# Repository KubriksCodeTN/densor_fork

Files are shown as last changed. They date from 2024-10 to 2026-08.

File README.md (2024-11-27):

# Densor



## About the project

Densor is an intraoral sensor platform, attached to regular dental retainers or aligners, that can take measurements inside the mouth. 

## Rationale

At present, in mouth measurements are typically made with external tools and in a controlled labaratory setting. Thus, real data from users daily lives is missing. To overcome this, we propose using widely used deltal retainers (or aligners), and enhance them with the Densor sensing platform. This way data is collected from inside the mouth without external tools. 

## Features

1. **Contactless transmission:** Densor is completely sealed and interacts with a smartphone via [NFC protocol](https://en.wikipedia.org/wiki/Near-field_communication). 
2. **Energy harvesting:** To stay powered Densor harvests energy, either from the [NFC communication itself](https://github.com/TUDSSL/densor/tree/master/NFC_harvester_battery_free) or from the [temperature gradient between the body and cold water](https://github.com/TUDSSL/densor/tree/master/TEG_harvester_battery_free). 
4. **Free of external hardware:** Operating Densor does not require any specialized tools, other than a NFC-compatible smartphone.

## Project layout

This repository contains the design (both hardware and software) of two versions of Densor, based on the source of energy harvesting. Each version of the project is contained in its own folder:

1. **[Densor with NFC-based energy harvesting from a smartphone](https://github.com/TUDSSL/densor/tree/master/NFC_harvester_battery_free)**, as presented in [this research article](https://dl.acm.org/doi/10.1145/3699746);
2. **[Densor with thermoelectric energy harvesting from drinking cold water](https://github.com/TUDSSL/densor/tree/master/TEG_harvester_battery_free)**.

 

## Copyright

Copyright (C) 2024 TU Delft Embedded Systems Group/[Sustainable Systems Laboratory](https://github.com/TUDSSL).

MIT License or otherwise specified. See [license](https://github.com/TUDSSL/densor/blob/master/LICENSE.txt) file for details.

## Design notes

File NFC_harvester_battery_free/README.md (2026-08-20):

# Densor with NFC-based Energy Harvesting from a Smartphone

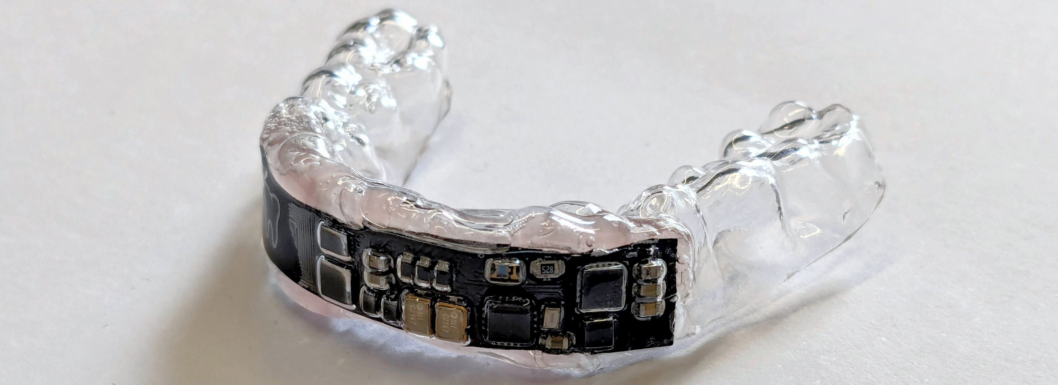
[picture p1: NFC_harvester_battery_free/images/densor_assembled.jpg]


This is the official public repository for intraoral sensing platform, called Densor (a portmanteau of a word _dental_ and _sensor_), based on [NFC protocol](https://en.wikipedia.org/wiki/Near-field_communication) for energy harvesting and communication from a NFC-enabled smartphone. For a Densor version with thermoelectric energy harvesting from drinking cold water please refer to [this repository](https://github.com/TUDSSL/densor/tree/master/TEG_harvester_battery_free). 

## About the Project

This repository contains the design files of the NFC-based Densor:

- [Densor hardware](https://github.com/TUDSSL/densor/tree/master/NFC_harvester_battery_free/hardware)
- [Densor firmware](https://github.com/TUDSSL/densor/tree/master/NFC_harvester_battery_free/software/DentalSensor_StorageProject)
- [Android app](https://github.com/TUDSSL/densor/tree/master/NFC_harvester_battery_free/software/source_ST25NFCApplication_V3_9)
- [Experiment setup and data collected from Densor evaluation](https://github.com/TUDSSL/densor/tree/master/NFC_harvester_battery_free/data/experiments) presented in Densor's [accompanying publciation](https://dl.acm.org/doi/10.1145/3699746).

## Rationale behind Densor

Intraoral sensors are another type of sensors in the field of healthcare and technology. While head-worn wearables have made significant advancements in monitoring various health metrics, placing sensors directly in the mouth remains a challenge. Currently, we rely heavily on external tools to gather dental and oral health data, which leaves critical information missing. For those looking to deploy in-mouth sensors, the process is daunting, requiring them to start from scratch. Additionally, there is no straightforward way to keep these sensors small, safe, and capable of long-lasting communication, making it difficult to integrate them into practical applications.

## Challenges

Intraoral sensing is unique because it operates within one of the most dynamic and challenging environments in the human body—the mouth. Unlike other forms of wearable technology, intraoral sensors must contend with constant exposure to saliva, varying temperatures, and the mechanical forces of chewing and speaking. These sensors need to be not only highly sensitive and accurate but also biocompatible and safe for long-term use. Additionally, they offer the potential to gather real-time data on oral health, dietary habits, and even health conditions, providing insights that are difficult to obtain through external sensors. This makes intraoral sensing a powerful tool with unique capabilities that go beyond existing methods.

## Densor Architecture

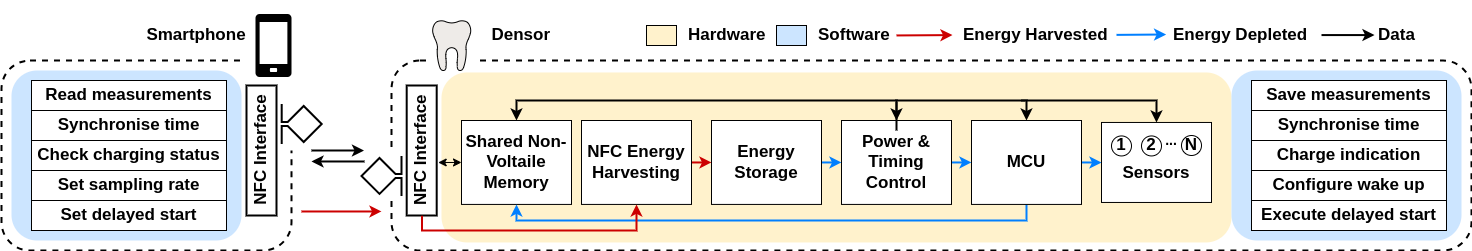
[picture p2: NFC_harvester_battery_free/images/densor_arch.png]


### Communication and Data Storage

Densor uses the NFC interface (based on STMicroelectronics' [ST25DV64K](https://www.st.com/en/nfc/st25dv64k.html) NFC/RFID tag IC) for communication with a smartphone, and the on board non-voltatile memory to store measurements. This way, data collected by Densor is always available to be read out by the smartphone.

### Energy Harvesting

Energy is harvested from the NFC tag itself, and stored for later use. This allows for Densor's continous operation and reader-independent data collection.

### Energy Storage

The harvested energy is stored on capacitors instead of batteries. This makes Densor a battery-free device and thus safer and more acceptable than Densor based on batteries.

### Power Control

Despite using low-power sensors, energy would be drained from the storage capacitor(s) rapidly if Densor is kept continuously powered. As the harvested energy stored on the capacitors is limited, it is imperative that we save and expend this power carefully. To overcome this, we use a low power Real-Time Clock (RTC) [AB1805](https://abracon.com/Precisiontiming/AB18X5-RTC.pdf) with power switch for power management. This means that the microcontroller unit (MCU) and sensors are completely powered off in the inter-sample period, with only the RTC powered to determine wake up time. This method achieves better power saving than deep-sleep or any of the low power run modes of the MCU.

### Densor On-Board Sensors

As of now, Densor includes three sensing modalities: temperature, accelaration and light intensity. Measuring oral temperature, jaw position, and whether the mouth is open using intraoral sensors is useful for gaining insight into oral and overall health. Oral temperature sensors provide accurate readings to detect early signs of fever and inflammation. Jaw position sensors can monitor alignment and movement, making them valuable for detecting sleep patterns. Light sensors that detect whether the mouth is open can help track breathing patterns and oral habits, which are essential for identifying issues like mouth breathing or sleep-related disorders.

## Densor Operation

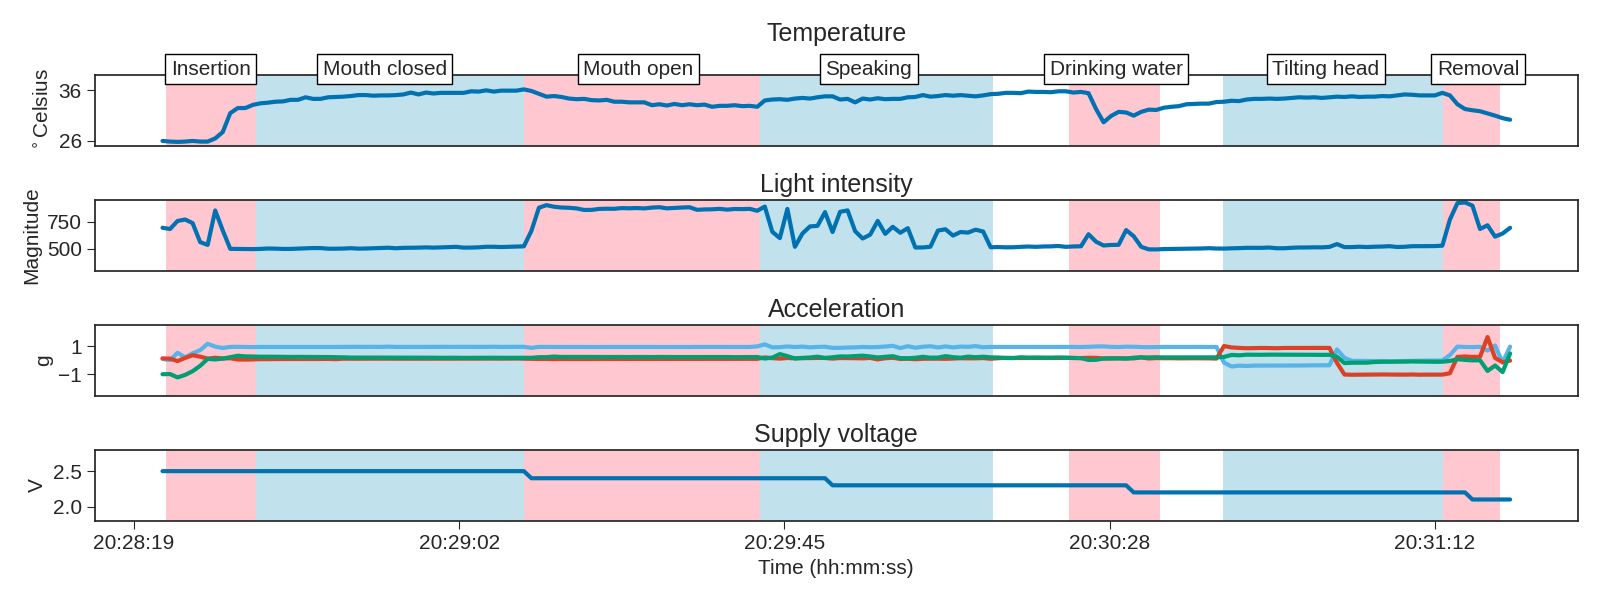
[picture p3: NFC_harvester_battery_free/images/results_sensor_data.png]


The above image shows examples of data collected by Densor and demonstrates its capabilities. The temperature can be seen rising to body temperature when Densor is inserted in the mouth. The light level falls when the mouth is closed, and rises when the mouth is open. It also varies when the user is speaking. When drinking cold water, the temperature initally falls and then rises back to body temperature.

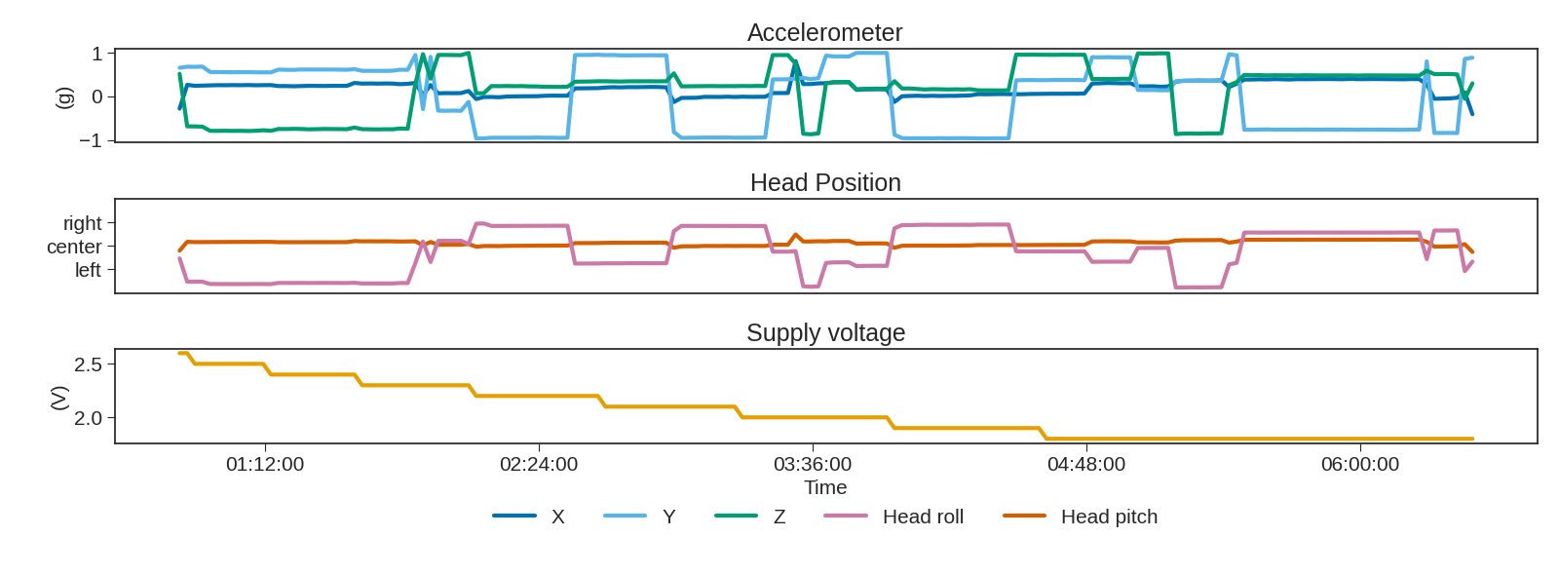
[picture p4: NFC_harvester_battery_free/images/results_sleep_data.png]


Densor can also determine the orientation of the jaw when the head is tilted. This is particularly useful for measuring head position during sleep, as seen in the above figure. The figure shows actual data collected from a user during a full night's sleep with _one sample collected every two minutes_. We can see the orientation of the head change between left, right and center as the user changes their sleep position.

## Getting Started with Densor

The long-term goal of the Densor project is to lower the ceiling of development of intraoral sensors. Thus, we wish that everyone can build, use and even expand Densor to improve sensing capabilities and data collection. Here we explain the steps to create Densor from scratch.

### Building the Densor Hardware

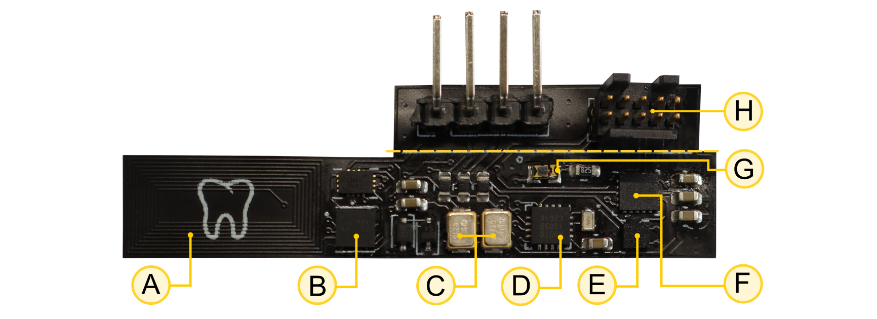
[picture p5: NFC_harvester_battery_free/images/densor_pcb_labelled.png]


The Densor printed circuit board (PCB) is built using off-the-shelf components and assembled onto a flexible PCB. In our case we have used the flex PCB services from [PCBway](https://www.pcbway.com/fpc-rigid-flex-pcb/flex-pcb.html). The picture above shows the main components of Densor ( (a comprehensive list of Densor hardware, along with links to buy them, can be found under [Hardware](https://github.com/TUDSSL/densor/tree/master/NFC_harvester_battery_free/hardware)).

- **A** Custom-designed PCB antenna
- **B** STMicroelectronics [ST25DV64K](https://www.st.com/en/nfc/st25dv64k.html) NFC tag
- **C** Seiko [CPH3225A](https://www.sii.co.jp/en/me/datasheets/chip-capacitor/cph3225a/) chip capacitor bank
- **D** Abracon [AB1805](https://abracon.com/Precisiontiming/AB18X5-RTC.pdf) RTC
- **E** STMicroelectronics [LIS2DW12](https://www.st.com/en/mems-and-sensors/lis2dw12.html) accelerometer
- **F** STMicroelectronics [STM32L021F4](https://www.st.com/en/microcontrollers-microprocessors/stm32l021f4.html) MCU
- **G** Vishay [VEMD1060X01](https://www.vishay.com/docs/84295/vemd1060x01.pdf) photodiode
- **H** Serial Wire Debug (SWD) programming port (which is cut off before embedding in a dental aligner).
- **I** TI [TMP117](https://www.ti.com/lit/ds/symlink/tmp117.pdf) temperature sensor

The [Densor hardware](https://github.com/TUDSSL/densor/tree/master/NFC_harvester_battery_free/hardware) folder contains the [gerber files](https://github.com/TUDSSL/densor/tree/master/NFC_harvester_battery_free/hardware/gerbers_schematic) which can be used to order the PCBs directly. To order directly, use the `.gbr` Gerber output files and `.drl` drill file for manufacturing.

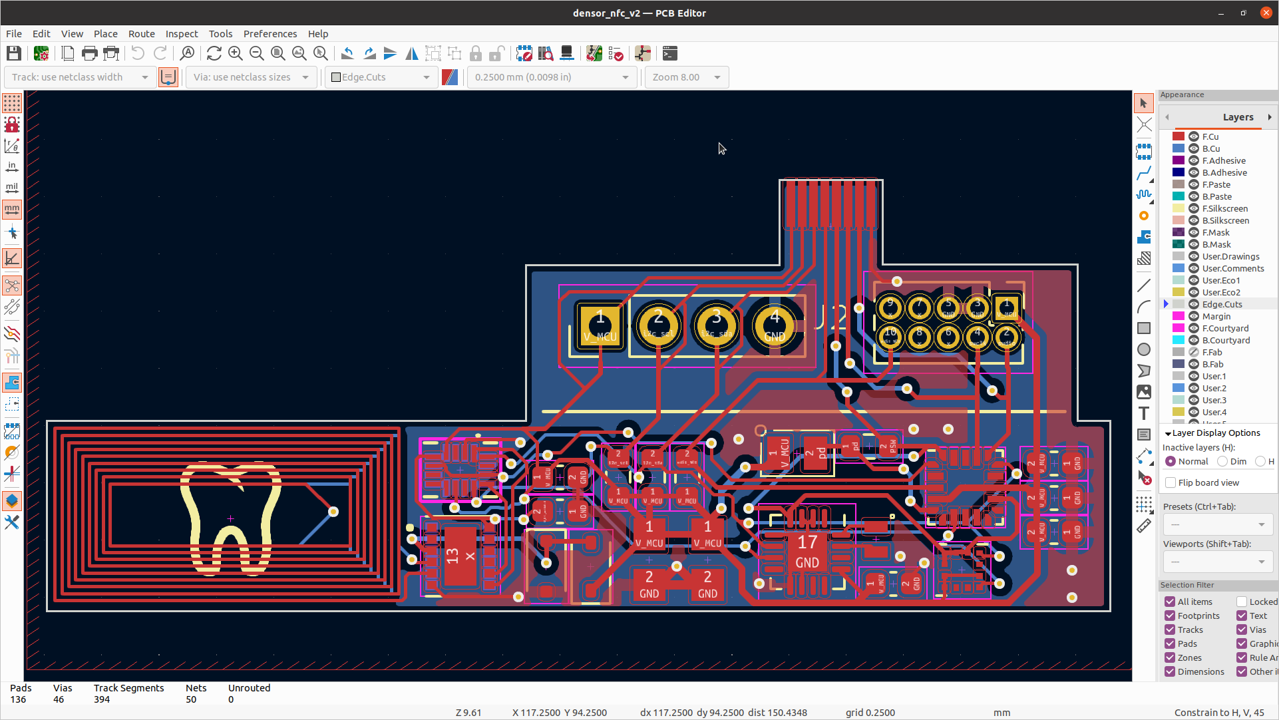
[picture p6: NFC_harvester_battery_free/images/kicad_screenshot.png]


The hardware folder also contains Densor' [schematic](https://github.com/TUDSSL/densor/tree/master/NFC_harvester_battery_free/hardware/gerbers_schematic) and [KiCad](https://www.kicad.org/blog/2021/12/KiCad-6.0.0-Release/) project which can be used for further expansion or modifications of Densor. A screenshot of the Densor PCB design in KiCad can be seen above. To open the project using Kicad, launch Kicad and navigate to 'File' -> 'Open project' -> And choose the [`densor_nfc_v2.kicad_pro`](https://github.com/TUDSSL/densor/blob/master/NFC_harvester_battery_free/hardware/Densor_kicad_project/densor_nfc_v2.kicad_pro) project file. The project includes the KiCad project files `.kicad_pcb`, `.pro` and `.sch`.

With the PCB and components, we used the lead-free [SAC305](https://nl.mouser.com/datasheet/2/73/SMD291SNL250T3-595229.pdf) solder paste to assemble the Densor as per the schematic.

### Uploading the Firmware to Densor's MCU

Once the Densor hardware is assembled, the [STM32L021F4](https://www.st.com/en/microcontrollers-microprocessors/stm32l021f4.html) MCU on board the Densor needs to have the firmware uploaded. The Densor [software folder](https://github.com/TUDSSL/densor/tree/master/NFC_harvester_battery_free/software/DentalSensor_StorageProject) contains the [STM32CubeIDE](https://www.st.com/en/development-tools/stm32cubeide.html)-based project is required for this. The firmware is uploaded using a [J-Link Debug probe](https://www.segger.com/products/debug-probes/j-link/) and a 10-pin header.

_Note:_ The current version of the PCB also has an [5034800800 FPC connector](https://www.molex.com/en-us/products/part-detail/5034800800) with all SWD signals which can also be used for programming.

### Memory Layout and Pinout

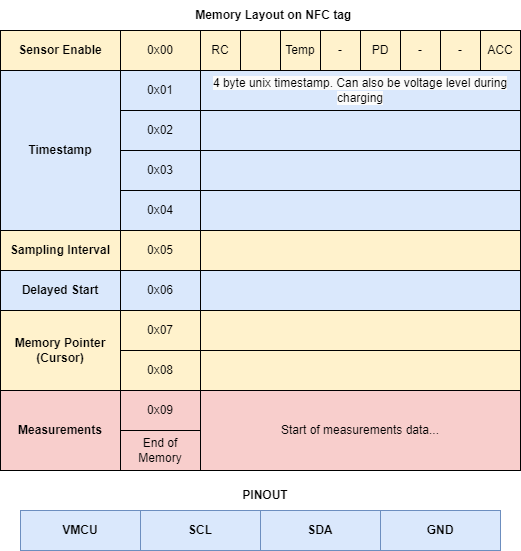
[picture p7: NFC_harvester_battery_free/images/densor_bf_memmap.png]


### Using the Densor Smartphone App

With the firmware uploaded to the MCU, the Densor is ready to be uses. This can be verified with an Android-based smartphone running the Densor [smartphone app](https://github.com/TUDSSL/densor/tree/master/NFC_harvester_battery_free/software/source_ST25NFCApplication_V3_9). The app (screenshot below) is built using Android Studio and can interact with the assembled Densor PCB via NFC. Detailed instructions on how to build the app can be found [here](https://github.com/TUDSSL/densor/tree/master/NFC_harvester_battery_free/software/source_ST25NFCApplication_V3_9).

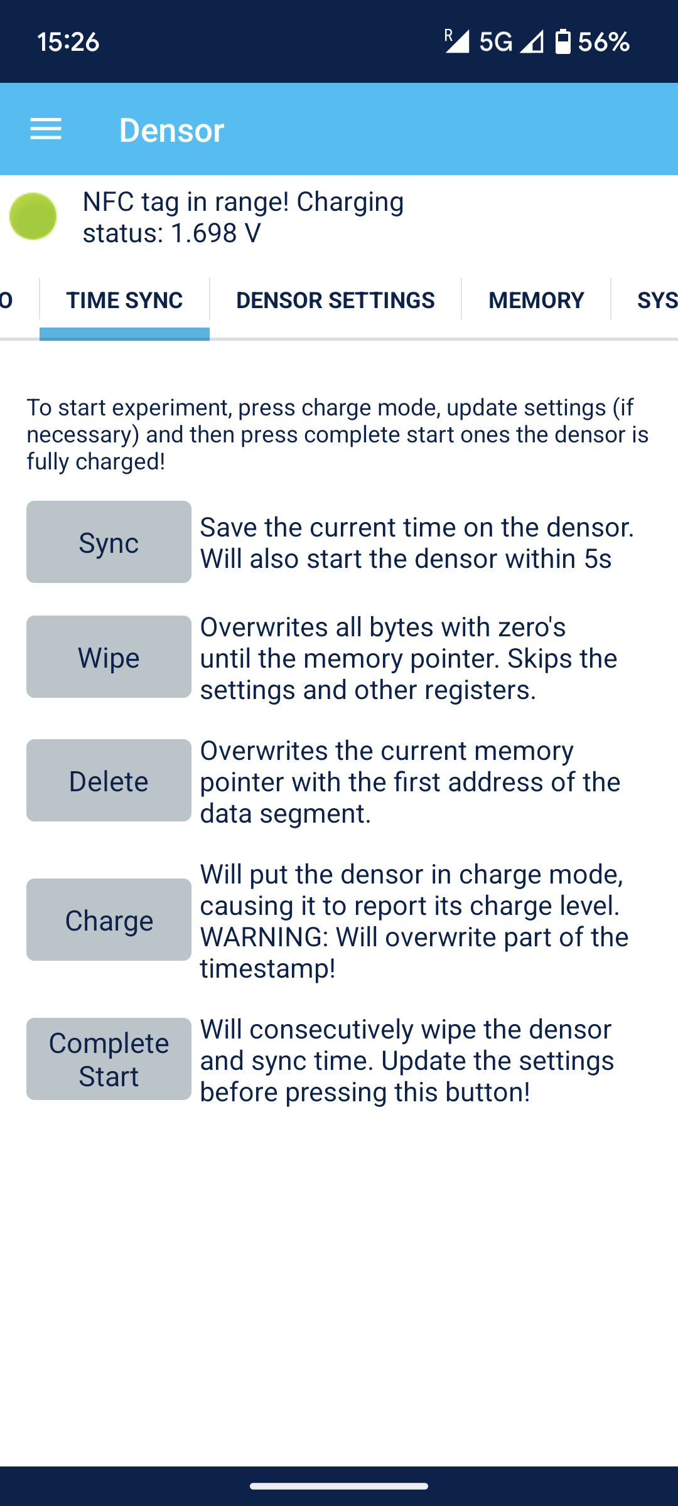
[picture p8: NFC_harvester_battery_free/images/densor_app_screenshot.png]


### Attaching Densor to Aligners using Epoxy

Finally, the Densor PCB has to be attached to the retiners or aligners. Clear plastic vaccum formed [retainers](https://en.wikipedia.org/wiki/Retainer_(orthodontics)) are widely used in orthodontic treatment. They can easily be fabricated with the help of a dental technician.

In our Densor fabrication process, first a [dental impression](https://en.wikipedia.org/wiki/Dental_impression) of each test subject was taken using [condensation silicone](https://products.coltene.com/EN/US/products/prosthetics/c-silicones/speedex/speedex-putty) placed on a dental impression tray. The hardened impression was later used to create a [plaster model](https://bredent-group.com/wp-content/uploads/2020/06/gipse-von-hoechster-Qualitaet_000727GB-20150601.pdf) of the subject's lower jaw teeth. Next, the plaster was placed inside an [Erkoform-3d+ dental  thermoforming unit](https://www.erkodent.de/en/product/?id=521210). Then, a dental [thermoforming plate](https://www.erkodent.de/wp-content/documents/products/thermoprosp_EN.pdf) was heated to 160 degrees Celcius by Erkoform-3d+, placed over the dental plaster and vacuum sealed. After vacuum sealing, all redundant and sharp edges of the fabricated aligner were removed by the cut-off wheel. The remaining imperfections were removed with the same cut-off wheel, and finally disinfected.

We used a [food safe epoxy](https://polyestershoppen.com/epoxy/voedselveilige-epoxy-419.html) to attach the assembled Densor PCB to the retainers. The epoxy has to be carefully mixed in a 10:6 ratio of resin and hardner, and applied over the PCB with a brush. The epoxy takes a _full five days to cure completely_ and must not be used before that even though it appears to have hardened.

**Once the epoxy is fully cured, Voila! You Densor is ready to use**.

## How to Operate Densor

To use Densor, begin with the smartphone app, and fully assembled Densor.

### Starting and Stopping Densor

_Step 1._ When you hold Densor close to the smartphone such that both NFC antennas of a Densor and a smartphone align, the app will launch automatically and Densor will begin charging.

_Step 2._ The capacitor's charged voltage will be displayed in the app. While Densor theoretically supports 3.3 V maximum capacitor voltage, in practice, it reaches about 2.6 V.

_Step 3._ To configure the on-board Densor sensors, go to the settings tab. Here, you can enable specific sensors, select the sampling rate, and set an optional delayed start. Click the `Update` button to apply these settings to the sensor.

_Step 4._ The Densor will only begin measuring once the time is synced. In the `Time Sync` tab, click the `Sync` button to start the sensor from the current time. The `Wipe` button deletes all previously collected data, while `Delete` resets the cursor without overwriting previous data with zeros.

_Step 5._ To stop the sensor, switch to `Charge` mode. This will revert the sensor to showing feedback on the charging voltage reached. _Note:_ This will also reset the timestamp. Please save measurements before putting Densor to charge mode.

### Reading the Data

_Step 1._ To save the data, go to the `Memory` tab and click `Dump memory to file`. In the 'Destination folder' field, enter your desired file name, then click `OK`. The data will be saved as a `.bin` file on your phone. The file is located in the 'Downloads' folder of the internal memory.

_Step 2._ To analyse this data, use the provided scripts avaible in the [data folder](https://github.com/TUDSSL/densor/tree/master/NFC_harvester_battery_free/data) of this repository.

_Step 3._ If the [experiment master](https://github.com/TUDSSL/densor/blob/master/NFC_harvester_battery_free/data/experiments/experiment_master_ui.py) script was used to generate the data as per a protocol, then place the generated `.bin` file in the [data dumps folder](https://github.com/TUDSSL/densor/tree/master/NFC_harvester_battery_free/data/experiments/data_dumps), and view the results with the [plot_labelled.py](https://github.com/TUDSSL/densor/blob/master/NFC_harvester_battery_free/data/experiments/plot_labeled.py) script. Make sure to use the [environment](https://github.com/TUDSSL/densor/blob/master/NFC_harvester_battery_free/data/environment.yml) provided.

## Collecting New Data

Data collected using Densor can be labelled and stored using the scripts in the [data folder](https://github.com/TUDSSL/densor/tree/master/NFC_harvester_battery_free/data/experiments).

1. **Using a predefined experiment protocol:** You can use a set of [existing experiment protocols](https://github.com/TUDSSL/densor/tree/master/NFC_harvester_battery_free/data/experiments/experiment_protocols) or create a new `.json` file to decide the tasks that will be performed while labeling data collected by Densor.
2. **Executing an experiment:** Run the [`experiment_master_ui.py`](https://github.com/TUDSSL/densor/blob/master/NFC_harvester_battery_free/data/experiments/experiment_master_ui.py) file to launch the instructing script. Perform the actions as instructed by the script for the prescribed duration.

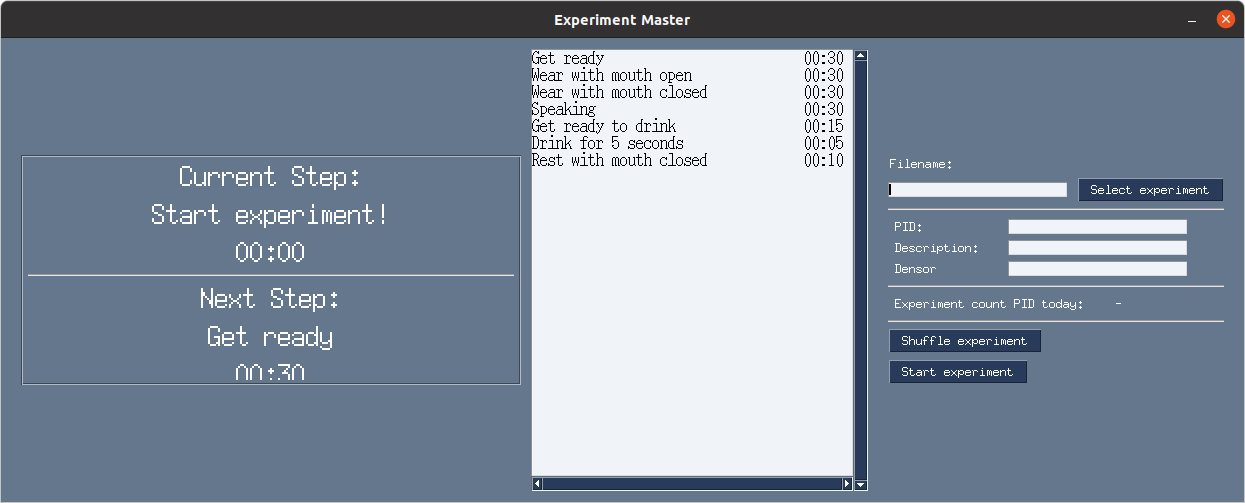
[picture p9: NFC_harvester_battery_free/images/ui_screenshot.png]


3. **Save the data:** Save the data using the smartphone app with the name prompted by the script to a `.bin` file and place it in the [data_dumps](https://github.com/TUDSSL/densor/tree/master/NFC_harvester_battery_free/data/experiments/data_dumps) folder.
4. **Label and view the data:** Run the `data_labeller.py` script to label the data for further machine learning tasks, or `plot_labelled.py` file to view the data.

## Frequently Asked Questions

**1. How long does it take to charge Densor?**

It takes approximately a minute to charge Densor using a smartphone. The exact charging time depends on how well the antennas of Densor and the smartphone align. The exact charging voltage of the capacitors can be read on the app for feedback.

**2. How long does Densor run when fully charged?**

Densor's lifetime depends on the sampling rate and number of capacitors used. For example, when using two capacitors and sampling once every two minutes Densor lasts for about 7 hours on a single charge. To increase the lifetime, more capacitors can be added. This will however change the charging behavior as well.

**3. Is Densor comfortable to wear?**

In our opinion, the experience of using Densor is no different than using retainers. Thus, if using retainers/aligners anyway, Densor should cause no additional discomfort beyond usinh the retainer.

**4. Will the mouth opening detection based on light intensity work when sleeping in the dark?**

Unfortunately, the mouth opening detection only works when there is sufficient ambient light. We are investigating ways to increase sensitivity for dark environments.

**5. Can I buy a Densor?**

Densor can be built with the design files in _this repository_. We desire Densor to be a free open source platform that can be rebuilt and expanded by everyone. If you wish to use (or expand) for your own research, please do not hesitate to contact us. We are happy to assist in reproduction efforts.

## How to Contribute to this Project

We look forward to your contributions, improvements, additions and changes. Please follow the standard [GitHub flow](https://docs.github.com/en/free-pro-team@latest/github/collaborating-with-issues-and-pull-requests/github-flow) for code contributions. In macro terms this means the following.

1. [Fork the `master` branch](https://docs.github.com/en/free-pro-team@latest/github/getting-started-with-github/fork-a-repo#keep-your-fork-synced)  of this repository; make sure that your fork will be [up to date](https://docs.github.com/en/free-pro-team@latest/github/getting-started-with-github/fork-a-repo#keep-your-fork-synced) with the latest `master` branch.
1. Create an issue [here](https://github.com/TUDSSL/densor/issues) with a new feature or a bug report.
1. Perform changes on your local branch and [push them to your forked clone](https://docs.github.com/en/free-pro-team@latest/github/collaborating-with-issues-and-pull-requests/merging-an-upstream-repository-into-your-fork).
1. Create a [pull request](https://docs.github.com/en/free-pro-team@latest/github/collaborating-with-issues-and-pull-requests/creating-a-pull-request) referencing the issue it covers and wait for our response.

### List of Known Issues

List of all known issues is listed in the [Issues](https://github.com/TUDSSL/densor/issues) list of this project. If you found a bug or you would like to enhance Densor with new functionalities: [please contribute](#How-to-Contribute-to-this-Project)! We look forward to your additions.

## How to Cite This Work

The results of this project have been published in a peer-reviewed academic publication (from which certain technical figures and text in this file originate). Details of the publication are as follows.

* **Authors and the project team:** [Vivian Dsouza](https://www.linkedin.com/in/dsouzavivian), [Jeffrey Pronk](https://www.linkedin.com/in/jeffrey-p-ba3225332), [Christian Peppelman](https://www.linkedin.com/in/peppelmanc), [Víctor Ignacio Madariaga](https://www.linkedin.com/in/vignaciomr), [Tatiana Pereira-Cenci](https://www.linkedin.com/in/tatiana-pereira-cenci-78813118/), [Bas Loomans](https://www.linkedin.com/in/bas-loomans-370ba11/), [Przemysław Pawełczak](http://www.pawelczak.net/)
* **Publication title:** _Densor: An Intraoral Battery-Free Sensing Platform_
* **Pulication venue:** [Proceedings of the ACM on Interactive, Mobile, Wearable and Ubiquitous Technologies, Volume 8, Issue 4, November 2024](https://dl.acm.org/toc/imwut/2024/8/4)
* **Link to publication:** https://dl.acm.org/doi/10.1145/3699746 (Open Access)

To cite this publication please use the following BiBTeX entry.

```
@article{dsouza:imwut:2024:densor,
  title = {Densor: An Intraoral Battery-Free Sensing Platform},
  author = {Vivian {Dsouza} and Jeffrey {Pronk} and Christian {Peppelman} and V\'{i}ctor Ignacio {Madariaga} and Tatiana {Pereira-Cenci} and Bas {Loomans} and Przemys{\l}aw {Pawe{\l}czak}},
  journal = {Proc. ACM Interact. Mob. Wearable Ubiquitous Technol.},
  volume = {8},
  number = {4},
  pages = {191:1--191:30},
  year = {2024},
  publisher = {ACM}
}
```

## Acknowledgements

We thank [Tofik Babayev](https://www.linkedin.com/in/tofik-babayev-36aa561a0) from [TofDent](https://www.tofdent.nl), The Hague, The Netherlands, for help in fabricating all versions of the Densor. We also thank [Giuseppe Deininger](https://www.linkedin.com/in/giuseppe-deininger-564a40153) and [Jakub Patałuch](https://www.linkedin.com/in/jakubpat) for contribution to the development of Densor at the initial states of the development. We also thank [Lennart Klaver](https://www.linkedin.com/in/lennart-klaver-19010945) for first attempts in designing intraoral sensor hardware, [Jasper de Winkel](https://www.linkedin.com/in/jdewinkel) for system design consulting and [Izabela Grudzińska](https://www.linkedin.com/in/grudzinskaizabela) for dentistry consulting and for the inspiration of this project. The study was partly funded by the [ORANGE-FORCE](https://www.nivel.nl/nl/project/orange-force-mond-en-tandheelkundige-zorg-voor-ouderen) project co-funded by the [PPP allowance](https://www.health-holland.com/public-private-partnerships) made available by [Health Holland](https://www.health-holland.com), [Top Sector Life Sciences and Health](https://www.academictransfer.com/en/employer/Health-Holland/).

 

## Copyright

Copyright (C) 2024 TU Delft Embedded Systems Group/[Sustainable Systems Laboratory](https://github.com/TUDSSL).

MIT License or otherwise specified. See [license](https://github.com/TUDSSL/densor/blob/master/LICENSE.txt) file for details.

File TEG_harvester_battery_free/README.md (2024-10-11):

# Densor - TEG harvester
A _Dental Sensor_ is a non-invasive, battery-less, intra-oral sensor. The Densor is embedded in the user's oral cavity and can measure temperature and orientation. It converts temperature differences caused by drinking into useful energy using two Thermal Electric Generators (TEGs).

### The Densor

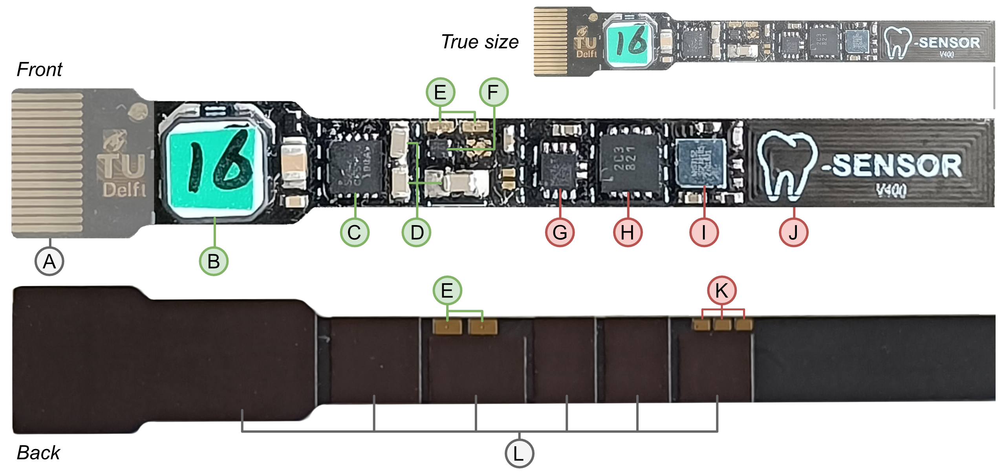
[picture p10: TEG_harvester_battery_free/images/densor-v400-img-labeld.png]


The figure above shows the final Densor prototype with several labelled components. All components of the Densor are placed on the front of the PCB to reduce complexity when assembling and provide a flat mounting surface. The PCB's bottom side only contains traces and several 0.15 mm polyimide stiffeners **L**. These stiffeners prevent stress on the component during bending and control where the PCB bends. This allows the PCB to bend to a very tight radius without stressing the delicate solder joints. 

The left side of the Densor contains a 14-pin FPC connector **A** used for development. This connector can be cut off once the development is done to reduce the Densors size. Next to the FPC connector, all harvesting components are placed together (labelled in green). The largest component, the LPR6235 coupled inductor **B**, is placed close to the Mercury energy harvester **C** and the three storage capacitors **D**. Two exposed soldering pads on the front and back of the Densor **E** are used to attach the TEGs to the Densor. The XC6136C18 voltage monitor **F** is placed between the harvesting and the sensing section. 

The sensing section (labelled in red) is centred around the NHS3152 microcontroller **I**. The microcontroller is surrounded by the decoupling capacitor, the pre-charge resistor and a voltage divider. On its left, the CY15B104 FRAM **H**, and LIS2DW12 accelerometer **G** are placed. The NFC antenna **J** is placed far away from the harvesting section and the SPI bus to reduce possible interference from the signal switching. The backside of the Densor contains three pads **K** that give access to the programming port of the MCU, even after the FPC connector is removed. 

The Densor has a length of 47.5 mm (without the FPC connector **A**), a width of 7 mm and a maximum height of 3.7 mm. 
The coupled inductor **B** mainly dictates the maximum width and height. Right of the inductor, the Densor is only 5 mm wide and has a maximum thickness of 1.25 mm.

_The full Densor schematic can be found in the hardware folder_

### The Development Board



The Densor's high component density and small size make developing with it challenging. The Densor has no room for test-pad, debugging interfaces or status LEDs. For this reason, a dedicated development board was created. The Densor can be mounted to this board using a single small pitch FPC connector. This gives the development board access to all relevant Densor signals like the SWD programming port, SPI bus and power lines. Once development is done, the FPC connector can be cut off the Densor to reduce its size.

The figure above shows the development board with a Densor mounted in the FPC connector **I**. A Raspberry Pi Pico **A** powers the development board via a micro USB cable and can act as a rudimentary logic analyser or USB-to-SPI bridge. The Pico has some bi-directional level shifters to interact with the Densor. The FPC connecter signals are attached to labelled test points next to the Densor **G**.

A 10-pin programming connector **B** is used to connect a SWD programmer to the Densor. With a 4-pole switch **C**, the programmer can be fully isolated from the Densor. This feature is used when testing the power consumption of the Densor since the programmer can influence these measurements. A reset and wake-up button **D** are placed close to the programming port. 

Several headers **E** allow easy access to the different supply lines and offer the option to power the Densor from the development board or the Power Profiler Kit II. A second header **F** allows to connect any signal to either of the three LEDs or the Pico logic analyser. The four screw headers at the top of the board **H** are used to connect to a power rail or a TEG. 

### Densor in Retainer

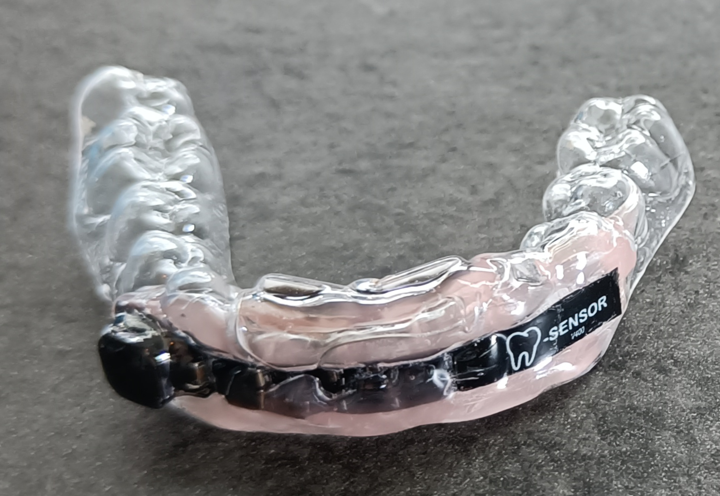
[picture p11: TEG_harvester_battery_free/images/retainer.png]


The figure above shows the Densor embedded in a retainer

## Copyright

 

Copyright (C) 2024 TU Delft Embedded Systems Group/Sustainable Systems Laboratory.

MIT Licence or otherwise specified. See [license](https://github.com/TUDSSL/ENGAGE/blob/master/LICENSE) file for details.

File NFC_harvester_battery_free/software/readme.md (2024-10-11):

# Densor - Software

## About the project 

This repository contains the design of Densor: an intraoral, actively powered, battery-free platform featuring multi-modal sensors and an extended lifespan. The repository consists of all components that make Densor:
- [Hardware](https://github.com/TUDSSL/densor/tree/master/NFC_harvester_battery_free/hardware)
- [Densor Firmware](https://github.com/TUDSSL/densor/tree/master/NFC_harvester_battery_free/software/DentalSensor_StorageProject)
- [Android app](https://github.com/TUDSSL/densor/tree/master/NFC_harvester_battery_free/software/source_ST25NFCApplication_V3_9)
- [Experiment setup and data collected](https://github.com/TUDSSL/densor/tree/master/NFC_harvester_battery_free/data/experiments)

This folder contains all the code related to the project i.e the firmware for the MCU , and the android app for the smartphone. 

## Folder layout

- **[STM32 CubeIDE Project - DentalSensor_StorageProject](https://github.com/TUDSSL/densor/tree/master/NFC_harvester_battery_free/software/DentalSensor_StorageProject):** contains the CubeIDE project for the STM32L021 MCU.
- **[Android App - source_ST25NFCApplication_V3_9](https://github.com/TUDSSL/densor/tree/master/NFC_harvester_battery_free/software/source_ST25NFCApplication_V3_9):** contains the Android Studio project to build the app.

## Running the software

1. **STM32 software**

Download and install [STM32CubeIDE](https://www.st.com/en/development-tools/stm32cubeide.html) from the official website. Then open the `DentalSensor_StorageProject` folder as a new project. Build and run the program with a debugger of your choice. In our case, the program is uploaded using a [J-Link Debug probe](https://www.segger.com/products/debug-probes/j-link/) and 10-pin header. The SWD programming pins can be used with other debugger/programmers (such as [ST-LINK](https://www.st.com/en/development-tools/st-link-v2.html) for example) with the required connections.

2. **Android app**

Follow the instructions [here](https://github.com/TUDSSL/densor/tree/master/NFC_harvester_battery_free/software/source_ST25NFCApplication_V3_9) to build and run the android app using Android studio. 

## Copyright

 

Copyright (C) 2024 TU Delft Embedded Systems Group/Sustainable Systems Laboratory.

MIT Licence or otherwise specified. See [license](https://github.com/TUDSSL/ENGAGE/blob/master/LICENSE) file for details.

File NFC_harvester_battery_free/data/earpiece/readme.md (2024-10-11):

# Earpiece
The earpiece is a tiny PCB containing a STMicroelectronics LIS2DW12 accelerometer. This PCB can be inserted in the ear using a commodity earplug to measure acceleration inside the ear canal. This PCB is used for the comparison between ear and mouth experiments.

## Fabrication
### Soldering
First, some solderpase is applied to the pads on the boards. Next, this solder paste is melted and equally distributed over the different pads using a soldering iron. Then, a hot air soldering station is used to re-melt the solder and apply the LIS2DW12 and its 100 nF decoupling capacitor. Finally, four wires are soldered to the connection pads which are used for power and data transfer.

### Sealing
To ensure the PCB is completely sealed, minimizing the risk of shorts and shocks, it is suspended in the air and covered in a thin layer of food grade epoxy. This is the same epoxy used for Densor. The particular epoxy used has a curing time of 3 days, after which the PCB can be used. The wires attached to the PCB are also partially coated in epoxy to strengthen them.

### Inserting
To make sure the PCB can sit comfortably in the ear, it is inserted inside a commodity earplug, normally used to block sound. The sound filter is removed from the plug by pulling it out and replaced with the PCB.

## Connection
The earpiece PCB is connected to an [Arduino Leonardo](https://docs.arduino.cc/hardware/leonardo/) which sets the accelerometer up correctly and then requests and reads a readings at a frequency of 25 Hz. The readings are then written on the serial bus of the Arduino. The firmware running on the system can be found at *lis2dw12_test_arduino.ino*

The Arduino is connected to a computer running the *serial_reader.py* script. This script takes the reading from the earpiece and writes it to a provided CSV file. (Note: the CSV file is overwritten. Please provide a name for a file that does not exist yet or can be overwritten.) The script is operated as follows:

`python serial_reader.py <path-to-serial-arduino> <path-to-csv-file>`

### Dependencies
The dependencies of the serial reader are:

- pyserial
- matplotlib

Both libraries are included in the conda environment for the Densor programs. This environment can be found at *../environment.yml*.

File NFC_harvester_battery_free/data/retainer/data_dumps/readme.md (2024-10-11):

# Data Dumps
All collected data from the retainers. This readme contains the meta data of the data dumps. </br>
Naming convention for the files: `yy-mm-dd-<test_subject>-<label>-<index>.bin`
- yy-mm-dd: date
- test_subject: p, followed by subject number. Subject number is 0 if no-one was wearing it.
  - label:
  - c: controlled test
  - s: sleeping
  - a: awake
  - i: intake
- index: index of the binary file, index per day, per user

## 24-03-13-p1-c-01
- Settings
	- 10 seconds interval
	- 0 delay
	- All sensors running
- Steps
	- 00:00: Inserting (3 samples), sitting still
	- 00:30: Closed mouth, head stable (3 samples)
	- 01:00: Open mouth, head stable (3 samples)
	- 01:30: Close mouth, head up (3 samples)
	- 02:00: Close mouth, head down (3 samples)
	- 02:30: Experiment finished, staying in. Talking and reading with densor inserted. (6 samples)
	- 03:30: Taking out. Into water.

## 24-03-13-p1-c-02
- Settings
	- 5 seconds interval
	- 0 delay
	- All sensors running
- Steps
	- 00:00 Inserting, sitting still
	- 01:00 Start talking, sitting stil
	- 02:00 Stop talking, start walking outside
	- 02:20 Enter stairs
	- 02:36: Leave stairs
	- 02:50: Went outside
	- 03:01: Bottom of stairs outside, started talking
	- 03:59: Back inside, stopped talking
	- 04:15: Enter stairs up
	- 04:34: Leave stairs

## 24-03-13-p1-a-03
- Settings
	- 10 seconds interval
	- 0 delay
	- All sensors running
- Steps
	- 00:00 Inserting, walks to office and works
	- 15:00 Goes outside and takes a walk
	- 35:00 Returns, works
	- 45:00 Returns to us, read out
- Issues
	- Only 2/3 read correctly

## 24-03-13-p1-a-04
- Settings
	- 45 seconds interval
	- 0 delay
	- All sensors running
- Steps
	- Wearing to lecture

## 24-03-18-p1-a-01
- Settings
	- 10 seconds interval
	- 0 delay
	- All sensors running
- Steps
	- Wearing in general. Working

## 24-03-18-p1-a-02
- Settings 
	- 30 seconds interval
	- 0 delay
	- All sensors running
- Steps
	- Wearing during work
	- Call at of 14 minutes, ended at 15:34

## 24-03-19-p1-s-01
- Settings 
	- 45 seconds interval
	- 0 delay
	- All sensors running
- Steps
	- Wearing overnight
	- Placed in mouth at 21:54

## 24-03-19-p1-a-02
- Settings
	- 45 seconds interval
	- 0 delay
	- All sensors running
- Steps
	- Wearing on the train
	- Train started moving 12:14
	- Left train 13:40
	- Bus started moving 13:42
	- Left bus 13:53
	- Walked up to office and took out

## 24-03-19-p0-c-01
- Settings
	- 10 seconds interval
	- 0 delay
	- All sensors running
	- Outside of mouth
- Steps
	- Verifying rotation
	- Started in right sleeping position
	- Moved slowely to left sleeping position, in steps between samples
	- Last sample to be discarded

## 24-03-21-p1-s-01
- Settings
	- 2 minutes interval
	- 0 delay
	- All sensors running
- Steps
	- Wearing overnight
	- Placed in mouth at 22:34

## 24-03-21-p0-s-01
- Settings
	- 2 minutes interval
	- 0 delay
	- All sensors running
	- Outside of mouth
	- Yellow board
- Steps
	- Started and left overnight, laying on desk in office

## 24-03-21-p0-c-02
- Settings
	- 1 second interval
	- 0 delay
	- All sensors running
	- Outside of mouth
	- Yellow board
- Steps
	- Dipped densor in cold water

## 24-03-22-p1-i-02
- Settings
	- 1 second interval
	- 0 delay
	- All sensors running
- Steps
	- Drinking cold water around 10:40

## 24-03-22-p1-s-01
- Settings
	- 2 minutes interval
	- 0 delay
	- All sensors running
- Steps
	- Wearing overnight
	- Placed in mouth at 23:40 

## 24-03-24-p1-i-03
- Settings
	- 1 second interval
	- 0 delay
	- All sensors running
- Steps
	- Drinking cold water

## 24-04-03-p0-c-01
- Settings
	- 59 minutes interval
	- 0 delay
	- All sensors running
- Steps
	- Laying on desk, not wearing
	- Checking runtime with maximum interval

## 24-04-16-p2-a-01
- Settings
	- 10 second interval
	- 0 delay
	- All sensors running
- Steps
	- Checking if densor works. First reading for p2
	- Opening and closing mouth, keeping mouth closed, opening and closing mouth.

## 24-04-16-p3-a-01
- Settings
	- 10 seconds interval
	- 0 delay
	- All sensors running
- Steps
	- Checking if densor works. First reading for p3
	- Opening and closing mouth consecutively

## 24-04-16-p3-a-02
- Settings
	- 1 second interval
	- 0 delay
	- All sensors running
- Steps
	- Only string light on, no sun light. String light positioned on right sight of the user.
	- Starting after 1 minute, laying on right and moving to center and left. Staying in every position for roughly 15 seconds.
		- mouth constantly open
	- started after 2 minutes with lights off, on right side, mouth open
		- moved to center and left after 15 seconds each
		- for the final 15 seconds, moved back to right and closed mouth.

## 24-04-16-p3-a-03
- Settings
	- 1 second interval
	- 0 delay
	- All sensors running
- Steps
	- First 30 seconds setup
	- Done with room lights instead of string light
	- With all steps 10 seconds long:
		- Right, mouth open
		- Right, mouth closed
		- Center, mouth open
		- Center, mouth closed
		- Left, mouth open
		- Left, mouth closed
	- Switch lights off for 10 seconds, then with all steps 10 seconds long:
		- Right, mouth open
		- Right, mouth closed
		- Center, mouth open
		- Center, mouth closed
		- Left, mouth open
		- Left, mouth closed

## 24-04-16-p3-a-04
- Settings
	- 1 second interval
	- 0 delay
	- All sensors running
- Steps
	- First 10 seconds setup
	- Done with room lights
	- Every step took 10 seconds
	- Opened mouth, facing light from roughly 2.5 meters away
	- Closed mouth, still facing light
	- Moved around, back facing light, mouth opened
	- Back facing light, mouth closed

## 24-04-25-p1-s-01
- Settings
	- 2 minutes interval
	- 0 delay
	- All sensors running
- Steps
	- Wearing overnight
	- Inserted at 00:49
	- Taken out at 8:20
	- Also used in machine learning, inserted hear for plotting sleep trace for paper.

## 24-04-25-p2-e-11
- Settings
	- 1 second interval
	- 0 delay
	- All sensors running
- Steps
	- Used to plot all tasks for paper
	- Consecutively, all step 30 seconds:
		- Wear with mouth closed
		- Wear with mouth opened
		- Speaking
		- Drinking (get ready 15s, drink 5s, put back glas 10s)
		- Tilting head from left to right

## 24-04-26-p2-s-01
- Settings
	- 2 minutes interval
	- 0 delay
	- All sensors running
- Steps
	- Wearing overnight
	- Placed in mouth at 22:57
	- Taken around 23:57

## 24-07-18-p2-c-01
- Settings
	- 1 second interval
	- 0 delay
	- All sensors running
- Steps
	- Opened and closed mouth in a dark room 
	- To evaluate if there is any difference in the dark

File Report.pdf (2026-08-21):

# Assignment Report

Patrick Pastorelli

August 21, 2026

## 1 1. Objective and Context

The objective of this assignment was to expand the design by integrating a suitable body temperature sensor into the battery-free Densor project. Initially, my first candidate was the Sensirion SHT4x family of temperature and humidity sensors, as I already have experience with these sensors and have developed multiple I²C drivers for different platforms. However, although the SHT4x provides both temperature and humidity measurements, its accuracy is not ideal for precise body temperature monitoring. Moreover, while humidity could potentially provide useful information for the project, measuring air humidity inside the mouth is not necessarily the most appropriate approach. A more suitable solution for oral wetness would be a dedicated wetness sensor, for example based on electrodes.

Based on these considerations, I conducted further research and identified the TI TMP117 and ADI MAX30205 as two high precision temperature sensors that could also meet the requirements of an ASTM E1112 compliant system. After further comparison, I selected the TMP117, as it offers lower power consumption and comes in a smaller package while still providing up to ±0.1

◦C accuracy over the operating temperature range of this application.

## 2 Schematic and PCB integration

For the integration, the TMP117 was added to the schematic with a 100 nF decoupling capacitor and connected to SCL, SDA, and VMCU. The interrupt pin was left floating, as it is not required by the firmware. The same form factor was maintained for the PCB layout. Both the schematic and the PCB layout were designed following the recommendations provided in the TI datasheet.

## 3 Firmware integration

To ensure a modular approach, a dedicated driver for the TMP117 was developed on top of the STM32 HAL, which was already included in the original firmware. Since the MCU has limited memory resources, the driver was kept barebones, containing only the necessary macros and the implementations of the readReg() and writeReg() functions. The firmware was extended in the following ways:
- A bit in the SensorEnable bitmap of the NFC tag was reserved for the TMP117, and the corresponding firmware checks were updated accordingly.
- The sensor initialization was added. The TMP117 is kept in shutdown mode and switched to one-shot mode only when a temperature measurement is required for the periodic data transaction. Polling was preferred over the interrupt line due to the short conversion time, while also avoiding the need to include the sleep mode HAL layers in the firmware.

Additionally, while this has not been actively done, the sensor can be easily calibrated to compensate for unforeseen noise after testing. Lastly, although the code could not be tested due to the unavailability of the hardware, it was fully documented and a Doxygen configuration file was added to generate the corresponding HTML documentation, the added firmware modifications are in /* ASSIGNMENT CODE BEGIN */ areas.

## 4 AI usage disclaimer

LLM models were used to get an initial idea of the schematic organization and for proofreading the grammar of this report. All chat histories can be found in the Extra folder.

1

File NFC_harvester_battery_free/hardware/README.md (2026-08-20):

# Densor - Hardware

## About the project 

This repository contains the design of Densor: an intraoral, actively powered, battery-free platform featuring multi-modal sensors and an extended lifespan. The repository consists of all components that make Densor:
- [Hardware](https://github.com/TUDSSL/densor/tree/master/NFC_harvester_battery_free/hardware)
- [Densor Firmware](https://github.com/TUDSSL/densor/tree/master/NFC_harvester_battery_free/software/DentalSensor_StorageProject)
- [Android app](https://github.com/TUDSSL/densor/tree/master/NFC_harvester_battery_free/software/source_ST25NFCApplication_V3_9)
- [Experiment setup and data collected](https://github.com/TUDSSL/densor/tree/master/NFC_harvester_battery_free/data/experiments)

This folder contains all the harware design files.

## Folder layout

- [Densor Kicad Project](https://github.com/TUDSSL/densor/tree/master/NFC_harvester_battery_free/hardware/Densor_kicad_project) contains the KiCad design files and can be opened with KiCad Version 8.
- [Datasheets](https://github.com/TUDSSL/densor/tree/master/NFC_harvester_battery_free/hardware/datasheets) contains the relavant datasheets of components used.
- [Gerbers Schematic](https://github.com/TUDSSL/densor/tree/master/NFC_harvester_battery_free/hardware/gerbers_schematic) contains the hardware output gerber files and schematic file in _.pdf_ format. This is useful if you wish to build Densor without any changes to the hardware.  

## List of components

| Component                  | Qty | Purchased from                                                                                                                                                                                                            |
|----------------------------|-----|---------------------------------------------------------------------------------------------------------------------------------------------------------------------------------------------------------------------------|
| Storage Capacitor          | 2   | [link to buy](https://www.digikey.com/en/products/detail/seiko-instruments/CPH3225A/8692444)                                                                                                                              |
| Decoupling Capacitor 100nF | 6   | [link to buy](https://nl.farnell.com/en-NL/kemet/c0603x104m4ractu/cap-mlcc-0-1uf-16v-0603/dp/2904941?st=0603%200.1uf)                                                                                                     |
| Zener Diode                | 1   | [link to buy](https://nl.farnell.com/on-semiconductor/mm3z3v6c/zener-diode-0-2w-3-6v-sod-323f/dp/2824925?CMP=i-ddd7-00001003)                                                                                             |
| Schottky Diode             | 1   | [link to buy](https://nl.farnell.com/nexperia/1ps76sb40-115/diode-schottky-sod323/dp/1349646?CMP=i-ddd7-00001003)                                                                                                         |
| Photo Diode                | 1   | [link to buy](https://nl.mouser.com/ProductDetail/Vishay-Semiconductors/VEMD1060X01?qs=pdQl6rENvLQkGyXPnNHd%2FQ%3D%3D&gclid=Cj0KCQjwmvSoBhDOARIsAK6aV7gSam9QYNxRe1G3dFcvfZGu4WvhXWOQdtZbTP3WNCzxGxyePn8TLa0aAiUbEALw_wcB) |
| Debug header               | 1   | [link to buy](https://nl.farnell.com/samtec/ftsh-105-01-l-d-k/connector-header-10pos-2row-1/dp/2856435?CMP=i-ddd7-00001003)                                                                                               |
| FPC connector              | 1   | [link to buy](https://nl.mouser.com/ProductDetail/Molex/503480-0800?qs=bodV9ulq6Gz33SKuZL445g%3D%3D&srsltid=AfmBOoqTYanmI1YXInVOzdpLIJ4tpVXYK3TQdvr3HJ4Y6jSj3ONDx022)                                                     |
| Pin Header 01x04           | 1   | [link to buy](https://nl.mouser.com/ProductDetail/Harwin/M20-9770446?qs=ulE8k0yEMYbCPpMPHeYh4w%3D%3D)                                                                                                                     |
| Resistor 100kohm           | 3   | [link to buy](https://nl.farnell.com/vishay/crcw0603100kfkea/res-100k-1-0-1w-0603-thick-film/dp/1469649?st=0603%20100k)                                                                                                   |
| Resistor 8Mohm             | 1   | [link to buy](https://nl.farnell.com/vishay/crcw06038m06fkea/res-8m06-1-0-1w-0603-thick-film/dp/2138717)                                                                                                                  |
| NFC Tag - ST25DV04K-JFR6D3 | 1   | [link to buy](https://www.digikey.nl/en/products/detail/stmicroelectronics/ST25DV64K-JFR6D3/7312974)                                                                                                                      |
| RTC - AM1805               | 1   | [link to buy](https://nl.farnell.com/en-NL/abracon/ab1805-t3/real-time-clock-i2c-qfn-16/dp/2467703?st=ab1805)                                                                                                             |
| MCU - STM32L021F3Ux        | 1   | [link to buy](https://www.digikey.nl/en/products/detail/stmicroelectronics/STM32L021F4U6TR/6166967)                                                                                                                       |
| Accelerometer - LIS2DW12   | 1   | [link to buy](https://nl.farnell.com/en-NL/stmicroelectronics/lis2dw12tr/lga-12-i-mems-digital-o-p-motion/dp/2849615?st=LIS2DW12TR)                                                                                       |
| SPDT - TS3A44159           | 1   | [link to buy](https://www.digikey.nl/en/products/detail/texas-instruments/TS3A44159RSVR/1909585)                                                                                                                          |
| Temperature sensor - TMP117AIDRVR | 1  | [link to buy](https://www.mouser.it/en/ProductDetail/Texas-Instruments/TMP117AIDRVR?qs=qSfuJ%252Bfl%2Fd6nh9h5HydMXQ%3D%3D) |
| Crystal                    | 1   | [link to buy](https://nl.farnell.com/en-NL/abracon/abs05w-32-768khz-j-2-t/crystal-32-768khz-4pf-smd-1-6/dp/2850126?st=abs05w)                                                                                             |
| Solder paste               | -   | [link to buy](https://www.digikey.nl/en/products/detail/chip-quik-inc/SMD291SNL50T3/5130160)                                                                                                                              |

## Copyright

 

Copyright (C) 2024 TU Delft Embedded Systems Group/Sustainable Systems Laboratory.

MIT Licence or otherwise specified. See [license](https://github.com/TUDSSL/ENGAGE/blob/master/LICENSE) file for details.

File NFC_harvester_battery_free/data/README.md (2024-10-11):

# Densor - Data 

## About the project 

This repository contains the design of Densor: an intraoral, actively powered, battery-free platform featuring multi-modal sensors and an extended lifespan. The repository consists of all components that make Densor:
- [Hardware](https://github.com/TUDSSL/densor/tree/master/NFC_harvester_battery_free/hardware)
- [Densor Firmware](https://github.com/TUDSSL/densor/tree/master/NFC_harvester_battery_free/software/DentalSensor_StorageProject)
- [Android app](https://github.com/TUDSSL/densor/tree/master/NFC_harvester_battery_free/software/source_ST25NFCApplication_V3_9)
- [Experiment setup and data collected](https://github.com/TUDSSL/densor/tree/master/NFC_harvester_battery_free/data/experiments)

This folder contains all the scripts to collect, process and analyse the data using Densor, as well as the data collected itself.

## Folder layout

- [Charging:](https://github.com/TUDSSL/densor/tree/master/NFC_harvester_battery_free/data/charging)  contains the data traces of how densor charges with a smartphone. 
- [Earpiece:](https://github.com/TUDSSL/densor/tree/master/NFC_harvester_battery_free/data/earpiece) contains the scripts used to collect data from the ear piece for the experiments that compare Densor to a similar earable platform.
- [Experiments:](https://github.com/TUDSSL/densor/tree/master/NFC_harvester_battery_free/data/experiments) contains all scripts and data used for the machine learning experiments.
- [Retainer:](https://github.com/TUDSSL/densor/tree/master/NFC_harvester_battery_free/data/retainer) contains all scripts and data collected from the Densor that are not related to the machine learning experiments.

## Setting Up the Environment

To set up the Conda environment from the provided `.yml` file, follow these steps:

### 1. Ensure Conda is Installed

Make sure you have Conda installed on your system. If you don't have it installed, you can download and install it from the [official Anaconda website](https://www.anaconda.com/products/distribution) or by using [Miniconda](https://docs.conda.io/en/latest/miniconda.html) for a lighter version.

### 2. Clone the Repository

Clone this repository to your local machine if you haven't done so already:

```bash
git clone https://github.com/TUDSSL/densor.git
cd densor
```

### 3. Create the Environment from the .yml File

Use the following command to create a new environment from the environment.yml file:

```bash
conda env create -f environment.yml
```

### 4. Activating the environment

Use the following command to activate the environment:

```bash
conda activate densor
```

## Description of how figures in the paper were produced

1. **Figure 5: Charging characteristics:** Run the `plot_charging_traces.py' script

```bash
cd NFC_harvester_battery_free/data/charging/
python3 plot_charging_traces.py
```   

2. **Figure 6 (a,b,c): Power and Lifetime** Run the `math_model_life.py' script

Set the below variables to True, based on the desired output
```
PLOT_CAPS = True
PLOT_CURRENT = False
PLOT_START_VOLTAGE = False
```

```bash
cd NFC_harvester_battery_free/data/charging/
python3 math_model_life.py
```   

3. **Figure 7: Example data from all sensors** Run the `plot_pretty_manually.py` script

```bash
cd NFC_harvester_battery_free/data/retainer/
python3 plot_pretty_manually.py
```
4. **Figure 10: Distribution of temperature and light intensity** Run the `data_ml.py` script with variable `plot_box_plots = True`
   
```bash
cd NFC_harvester_battery_free/data/experiments
python3 data_ml.py
```
5. **Figure 11 (a,b,c): Data from Densor and Earable** Run the `plot_ear_mouth_example_trace.py' script with arguments as explained [here](https://github.com/TUDSSL/densor/tree/master/NFC_harvester_battery_free/data/experiments).
6. **Figure 12: ROC** Run the `data_ml.py` script with variable `plot_roc_curve = True`

```bash
cd NFC_harvester_battery_free/data/experiments
python3 data_ml.py
```
7. **Figure 13: Example data from sleep** Run the `plot_pretty_sleep_manually.py` script

```bash
cd NFC_harvester_battery_free/data/retainer/
python3 plot_pretty_sleep_manually.py
```

## Copyright

 

Copyright (C) 2024 TU Delft Embedded Systems Group/Sustainable Systems Laboratory.

MIT Licence or otherwise specified. See [license](https://github.com/TUDSSL/ENGAGE/blob/master/LICENSE) file for details.

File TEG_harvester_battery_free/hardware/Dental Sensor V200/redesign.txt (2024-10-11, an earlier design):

- 23-11-2022 CP: Add tuning capacitor to NFC-antenna
- 23-11-2022 CP: WAKEUP/PIO0_0 of NHS3152 should not be connected to INT1
					- INT 1 is a push-pull pin (to ground by default), this disables the button on the dev-board
					- Draws excessive when in power-down mode (250 uA instead of 3.4 uA)
- 23-11-2022 CP: Add method to wake NHS after a power-off state
- 23-11-2022 CP: Add method to disable the I2C pull-ups, but leave VEXT on. (Pull-up are a majority of the current. New method would allow to wait for a interrupt)
- 24-11-2022 CP: I2C uses a lot of power and needs a high clock frequency. Look into using SPI instead
- 01-12-2022 CP: Optional: Add 1K precharge for VEXT.
- 09-12-2022 CP: Better 0402 footprints
- 16-12-2022 CP: Improve IMU footprint. Current one is hard to solder

- 23-11-2022 CP: (dev-board) I2C level shifting FET's are connected to VVDBAT without a jumper. Add a jumper between
- 24-11-2022 CP: (dev-board) SWD connector without sides (easier to disconnect)
- 24-11-2022 CP: (dev-board) Switch to disconnect SWD (useful when doing low power measurements)
- 24-11-2022 CP: (dev-board) Add more indication LED's
- 24-11-2022 CP: (dev-board) SOT Footprint of the FET is not correct

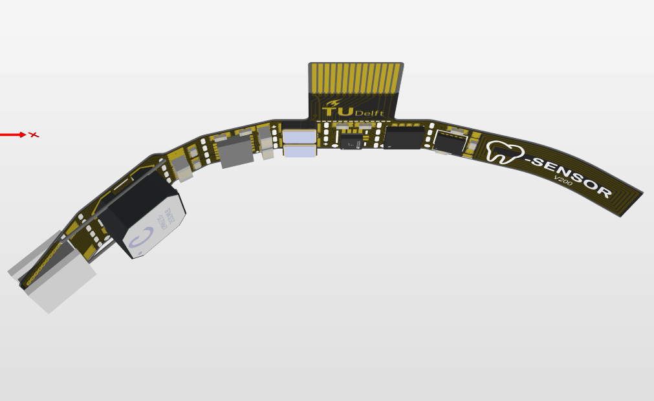
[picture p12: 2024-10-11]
TEG_harvester_battery_free/images/densor_v200_flexed.png

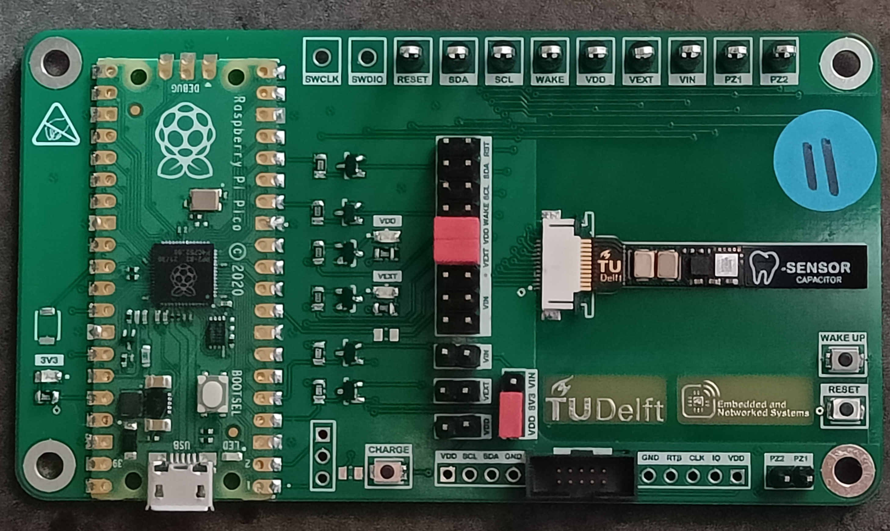
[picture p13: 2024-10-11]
TEG_harvester_battery_free/images/Densor.jpg

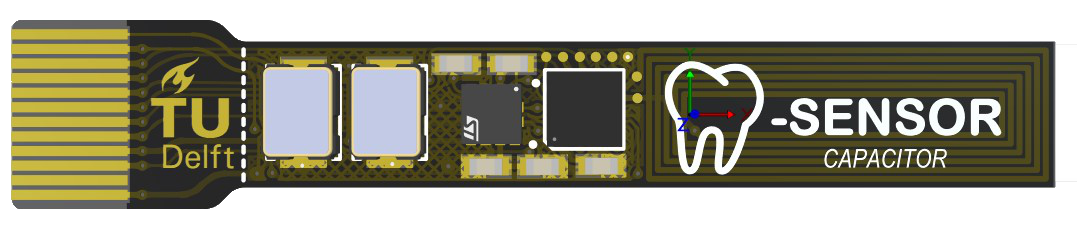
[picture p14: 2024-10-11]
TEG_harvester_battery_free/images/densor_capacitor.png

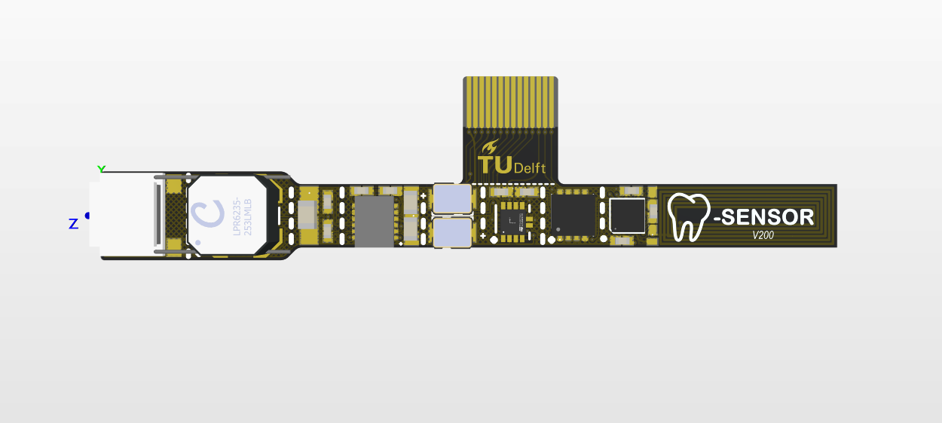
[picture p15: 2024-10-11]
TEG_harvester_battery_free/images/densor_v200.png

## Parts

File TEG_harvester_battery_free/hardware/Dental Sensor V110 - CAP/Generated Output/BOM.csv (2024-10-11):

Designator | Description | Comment | Quantity
C1, C3 | CAP CER 0.1UF 6.3V X5R 0402 | 0.10µF | 2
C2 | CAP CER 2.2UF 6.3V X5R 0402 | 2.2µF | 1
C4, C5 | Supercapacitors / Ultracapacitors Reflow EDLC 3.3V, 11mF, 160 Ohm | CPH3225A | 2
CN1 | FFC / FPC Board Connector, 0.5 mm, 12 Contacts, Receptacle, Easy-On 52745, Surface Mount, Top | FPC Connector | 1
R2, R3 | RES SMD 47K OHM 1% 1/10W 0402 | 47K | 2
TP1, TP2, TP3, TP4, TP7, TP8, TP9, TP10 |  | Testpoint | 8
U1 | ARM-microcontrollers - MCU NTAG NHS3152 NFC | NHS3152UK | 1
U2 | MEMS DIGITAL OUTPUT MOTION SENSO | AIS2DW12TR | 1

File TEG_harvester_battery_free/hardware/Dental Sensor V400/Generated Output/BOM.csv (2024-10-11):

Designator | Description | Comment | Quantity
C1 | CAP CER 100UF 2.5V X6S 0805 | 100µF | 1
C2 | CAP CER 4.7UF 6.3V X5R 0402 | 4.7µF | 1
C3, C6 | CAP CER 0.1UF 6.3V X5R 0402 | 0.10µF | 2
C4 | CAP CER 300PF 50V NP0 0402 | 300pF | 1
C5 | CAP CER 10UF 6.3V X5R 0402 | 10µF | 1
C7, C8 | CAP CER 47UF 6.3V X5R 0603 | 47µF | 2
C9 | Supercapacitors / Ultracapacitors Reflow EDLC 3.3V, 11mF, 160 Ohm | CPH3225A | 1
CN1 | FFC / FPC Board Connector, 0.5 mm, 16 Contacts, Receptacle, Easy-On 52745, Surface Mount, Top | FPC Connector | 1
D1, D2 | DIODE SCHTTKY 70V 70MA X1DFN1006 | BAS70LP-7B | 2
L1 | Gekoppelde smoorspoelen 12.5uH 12% 900mA 200 Ohms | LPR6235-123QMRC | 1
R1 | RES SMD 10K OHM 5% 1/10W 0402 | 10k | 1
R2 | RES SMD 1.5M OHM 5% 1/10W 0402 | 1.5M | 1
R3 | RES SMD 470K OHM 1% 1/10W 0402 | 470k | 1
U1 | ARM-microcontrollers - MCU NTAG NHS3152 NFC | NHS3152UK | 1
U2 | FRAM (Ferroelectric RAM) Memory IC 4Mbit SPI 20 MHz 8-GQFN (3.23x3.28) | CY15B104QI-20LPXC | 1
U3 | ACCEL 2-16G I2C/SPI 12LGA | LIS2DW12TR | 1
U4 | Matrix Mercury Energy Harvesting Synchronous Boost Converter with Microwatt Cold-Start, Input Impedance Matching and Regulated Output | MCRY12-125Q-33DIT | 1
U5 | Controlecircuits Ultra-Low Power (88nA) Voltage Detector | XC6136N18 | 1
U6 | Controlecircuits Ultra-Low Power (88nA) Voltage Detector | XC6136C19 | 1

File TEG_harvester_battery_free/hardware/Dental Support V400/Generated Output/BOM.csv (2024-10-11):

Designator | Description | Comment | Quantity
J1 | CONN HEADER VERT 10POS 1.27MM | SHF-105-01-L-D-TH | 1
J2 | THT Vertical Pin Header WR-PHD, Pitch 2.54 mm, Dual Row, 22 pins | 61302221121 | 1
J3 | 0.5 mm Pitch Easy-On(TM) Type FPC Connector, 2.0 mm Mated Height, Right Angle, ZIF, SMT, Top Contact, 16 Circuits, -20 to 85 degC, ELV and RoHS Compliant, Tape and Reel | 52745-1697 | 1
J4, J5, J6, J7 |  | MKDS 1/ 2-3,5 HT BK | 4
LED1, LED2, LED3, LED4 | LED RED CLEAR 0805 SMD | 150080SS75000 | 4
P1 | THT Vertical Pin Header WR-PHD, Pitch 2.54 mm, Single Row, 5 pins | 61300511121 | 1
P2, P4, P5, P6 | THT Vertical Pin Header WR-PHD, Pitch 2.54 mm, Single Row, 2 pins | 61300211121 | 4
P3, P7, P8 | THT Vertical Pin Header WR-PHD, Pitch 2.54 mm, Single Row, 3 pins | 61300311121 | 3
Q1, Q2, Q3, Q4, Q5, Q6, Q7, Q8, Q9, Q10 | MOSFET N-CH 50V 220MA SOT-23 | BSS138 | 10
R1, R2, R4, R16 | RES SMD 2K OHM 1% 1/8W 0805 | 2k | 4
R3, R5, R10, R11, R17 | RES SMD 100 OHM 1% 1/8W 0805 | 100 | 5
R6, R7, R8, R9, R12, R13, R14, R15, R18, R19 | RES SMD 10K OHM 1% 1/8W 0805 | 10k | 10
SW1, SW2, SW3 | SWITCH TACTILE SPST-NO 0.05A 12V | B3U-1000P | 3
SW4 | Pushbutton Switch SPST-NO Keyswitch, Illuminated Through Hole | ASE4204 | 1
TP1, TP2, TP3, TP4, TP5, TP6, TP7, TP8, TP9, TP10, TP11, TP12, TP13, TP14, TP15, TP16 | Test Point, Black, Through Hole, RoHS, Bulk | 5011 | 16
U1 |  | RPI Pico | 1

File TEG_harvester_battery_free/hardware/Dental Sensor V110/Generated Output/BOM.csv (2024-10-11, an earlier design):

Designator | Description | Comment | Quantity
C1, C3 | CAP CER 0.1UF 6.3V X5R 0402 | 0.10µF | 2
C2 | CAP CER 2.2UF 6.3V X5R 0402 | 2.2µF | 1
C4 | CAP CER 1UF 6.3V X7R 0402 | 1µF | 1
C5 | CAP CER 10UF 6.3V X5R 0402 | 10µF | 1
C6 | CAP CER 4.7UF 6.3V X5R 0402 | 4.7µF | 1
C7 | CAP CER 22UF 10V X5R 0603 | 22µF | 1
C8 | CAP CER 1000PF 6.3V X5R 0402 | 1000pF | 1
CN1 | FFC / FPC Board Connector, 0.5 mm, 12 Contacts, Receptacle, Easy-On 52745, Surface Mount, Top | FPC Connector | 1
L1 | Shielded Multilayer Inductor 10uH ±20% 300mA 780mO SMD 0603 | MLZ1608N100LT000 | 1
R1 | RES SMD 1M OHM 1% 1/10W 0402 | 1M | 1
R2, R3 | RES SMD 47K OHM 1% 1/10W 0402 | 47k | 2
TP1, TP2, TP3, TP4, TP6, TP7, TP8, TP9, TP10, TP11, TP12 |  | Testpoint | 11
U1 | ARM-microcontrollers - MCU NTAG NHS3152 NFC | NHS3152UK | 1
U2 | MEMS DIGITAL OUTPUT MOTION SENSO | AIS2DW12TR | 1
U3 | Piezoelectric Energy Harvesting Power Supply, 10-pin SON (DD-10), -40 to 125 degC, Pb-Free | LTC3588EDD-1#PBF | 1

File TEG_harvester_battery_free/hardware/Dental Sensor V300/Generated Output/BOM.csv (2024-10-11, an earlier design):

Designator | Description | Comment | Quantity
BT1, BT2, BT3 | Coin, 4.8mm 3V Lithium Battery Rechargeable (Secondary) 2mAh | MS414GE-FL26E | 3
C1, C3, C4 | CAP CER 0.1UF 6.3V X5R 0402 | 0.10µF | 3
C2 | CAP CER 300PF 50V NP0 0402 | 300pF | 1
C5, C6 | CAP CER 47UF 6.3V X5R 0603 | 47µF | 2
CN1 | FFC / FPC Board Connector, 0.5 mm, 14 Contacts, Receptacle, Easy-On 52745, Surface Mount, Top | FPC Connector | 1
R1 | RES SMD 47K OHM 1% 1/10W 0402 | 47k | 1
U1 | ARM-microcontrollers - MCU NTAG NHS3152 NFC | NHS3152UK | 1
U2 | FRAM (Ferroelectric RAM) Memory IC 4Mbit SPI 20 MHz 8-GQFN (3.23x3.28) | CY15B104QI-20LPXC | 1
U3 | ACCEL 2-16G I2C/SPI 12LGA | LIS2DW12TR | 1

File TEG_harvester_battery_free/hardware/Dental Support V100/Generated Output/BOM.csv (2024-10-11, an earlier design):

Designator | Description | Comment | Quantity
J1 | 0.5 mm Pitch Easy-On(TM) Type FPC Connector, 2.0 mm Mated Height, Right Angle, ZIF, SMT, Top Contact, 12 Circuits, -20 to 85 degC, ELV and RoHS Compliant, Tape and Reel | 52745-1297 | 1
J2 | THT Vertical Pin Header WR-PHD, Pitch 2.54 mm, Dual Row, 18 pins | 61301821121 | 1
LED1, LED2, LED3 | LED RED CLEAR 0805 SMD | 150080SS75000 | 3
P1 | THT Vertical Pin Header WR-PHD, Pitch 2.54 mm, Single Row, 5 pins | 61300511121 | 1
P2 | THT Vertical Pin Header WR-PHD, Pitch 1.27 mm, Dual Row, 10 pins | 62201021121 | 1
P3 | THT Vertical Pin Header WR-PHD, Pitch 2.54 mm, Single Row, 4 pins | 61300411121 | 1
P4, P5, P6, P7 | THT Vertical Pin Header WR-PHD, Pitch 2.54 mm, Single Row, 2 pins | 61300211121 | 4
P8, P9 | THT Vertical Pin Header WR-PHD, Pitch 2.54 mm, Single Row, 3 pins | 61300311121 | 2
Q1, Q2, Q3, Q4, Q5, Q6 | MOSFET N-CH 50V 220MA SOT-23 | BSS138 | 6
R1, R2, R4 | RES SMD 2K OHM 1% 1/8W 0805 | 2k | 3
R3, R5, R6, R7, R10, R11 | RES SMD 100 OHM 1% 1/8W 0805 | 100 | 6
R8, R9 | RES SMD 10K OHM 1% 1/8W 0805 | 10k | 2
SW1, SW2, SW3, SW4 | SWITCH TACTILE SPST-NO 0.05A 12V | B3U-1000P | 4
TP1, TP2, TP3, TP4, TP5, TP6, TP7, TP8, TP9, TP10, TP11 | Test Point, Black, Through Hole, RoHS, Bulk | 5011 | 11
U1 |  | RPI Pico | 1

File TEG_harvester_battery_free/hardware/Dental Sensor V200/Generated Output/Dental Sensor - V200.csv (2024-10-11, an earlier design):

Comment | Description | Designator | Footprint | LibRef | Quantity
0.10µF | CAP CER 0.1UF 6.3V X5R 0402 | C1, C3, C4 | RESC1005X03N | GRM155R60J104KA01D | 3
300pF | CAP CER 300PF 50V NP0 0402 | C2 | RESC1005X03N | GRM1555C1H301JA01D | 1
CPH3225A | Supercapacitors / Ultracapacitors Reflow EDLC 3.3V, 11mF, 160 Ohm | C5, C6 | CPH3225A | CPH3225A | 2
1000pF | CAP CER 1000PF 16V X5R 0402 | C7 | CAPC1005X03N | GRM155R61C102KA01D | 1
330pF | CAP CER 330PF 50V X7R 0402 | C8 | CAPC1005X03N | GRM155R71H331KA01J | 1
100µF | CAP CER 100UF 2.5V X6S 0805 | C9 | CAPC2012X12N | GRM21BC80E107ME15L | 1
47µF | CAP CER 47UF 6.3V X5R 0603 | C10, C12 | CAPC1608X12N | GRJ155R60J106ME11D | 2
1µF | CAP CER 1UF 16V X5R 0402 | C11 | CAPC1005X03N | GRT155R61C105KE01D | 1
FPC Connector | FFC / FPC Board Connector, 0.5 mm, 14 Contacts, Receptacle, Easy-On 52745, Surface Mount, Top | CN1 | 52745-1497 | 52745-1497 | 1
LPR6235-752SMRC | Gekoppelde smoorspoelen 7.5uH 75% 1.6A 316 Ohms 1:100 | L1 | LPR6235 | LPR6235-752SMRC | 1
47k | RES SMD 47K OHM 1% 1/10W 0402 | R1, R2 | CAPC1005X03N | ERJ-2RKF4702X | 2
NHS3152UK | ARM-microcontrollers - MCU NTAG NHS3152 NFC | U1 | WLCSP25 | NHS3152UK | 1
CY15B104QI-20LPXC | FRAM (Ferroelectric RAM) Memory IC 4Mbit SPI 20 MHz 8-GQFN (3.23x3.28) | U2 | 8-GQFN | CY15B104QI-20LPXC | 1
LIS2DW12TR | ACCEL 2-16G I2C/SPI 12LGA | U3 | FP-LGA12-DM00170568-MFG | CMP-12175-000006-1 | 1
LTC3108EDE#PBF | Ultralow Voltage Step-Up Converter and Power Manager, 12-pin SON (DE-12), -40 to 125 degC, Pb-Free | U4 | LT-DE-12-05-08-1708_V | CMP-0473-00079-1 | 1

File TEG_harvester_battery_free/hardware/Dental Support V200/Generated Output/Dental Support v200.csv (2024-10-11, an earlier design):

Comment | Description | Designator | Footprint | LibRef | Quantity
SHF-105-01-L-D-TH | CONN HEADER VERT 10POS 1.27MM | J1 | FP-SHF-105-01-L-D-TH-MFG | CMP-02766-000059-1 | 1
61302221121 | THT Vertical Pin Header WR-PHD, Pitch 2.54 mm, Dual Row, 22 pins | J2 | 61302221121 | CMP-1502-01108-1 | 1
52745-1497 | 0.5 mm Pitch Easy-On(TM) Type FPC Connector, 2.0 mm Mated Height, Right Angle, ZIF, SMT, Top Contact, 14 Circuits, -20 to 85 degC, ELV and RoHS Compliant, Tape and Reel | J3 | MOLX-52745-1497 | CMP-1241-00360-1 | 1
150080SS75000 | LED RED CLEAR 0805 SMD | LED1, LED2, LED3, LED4, LED5 | FP-150080SS75000-MFG | CMP-1426-00010-2 | 5
61300511121 | THT Vertical Pin Header WR-PHD, Pitch 2.54 mm, Single Row, 5 pins | P1 | 61300511121 | CMP-1502-01068-1 | 1
61300211121 | THT Vertical Pin Header WR-PHD, Pitch 2.54 mm, Single Row, 2 pins | P2, P4, P5, P6 | 61300211121 | CMP-1712-00002-4 | 4
61300311121 | THT Vertical Pin Header WR-PHD, Pitch 2.54 mm, Single Row, 3 pins | P3, P7, P8 | 61300311121 | CMP-1502-01062-1 | 3
BSS138 | MOSFET N-CH 50V 220MA SOT-23 | Q1, Q2, Q3, Q4, Q5, Q6, Q7, Q8, Q9, Q10 | FP-318-08-IPC_B | CMP-07173-000101-1 | 10
2k | RES SMD 2K OHM 1% 1/8W 0805 | R1, R2, R4, R16, R18 | RESC2012X06N | ERJ-6ENF2001V | 5
100 | RES SMD 100 OHM 1% 1/8W 0805 | R3, R5, R10, R11, R17, R19 | RESC2012X06N | ERJ-6ENF1000V | 6
10k | RES SMD 10K OHM 1% 1/8W 0805 | R6, R7, R8, R9, R12, R13, R14, R15 | RESC2012X06N | ERJ-6ENF1002V | 8
B3U-1000P | SWITCH TACTILE SPST-NO 0.05A 12V | SW1, SW2, SW3 | FP-B3U-1000P-MFG | CMP-2100-03586-2 | 3
ASE4204 | Pushbutton Switch SPST-NO Keyswitch, Illuminated Through Hole | SW4 | FP-ASE4204-MFG | CMP-03405-000007-1 | 1
5011 | Test Point, Black, Through Hole, RoHS, Bulk | TP1, TP2, TP3, TP4, TP5, TP6, TP7, TP8, TP9, TP10, TP11, TP12, TP13, TP14 | KSTN-5011_V | CMP-1672-00003-4 | 14
RPI Pico |  | U1 | RPI Pico | RPI Pico | 1
CP

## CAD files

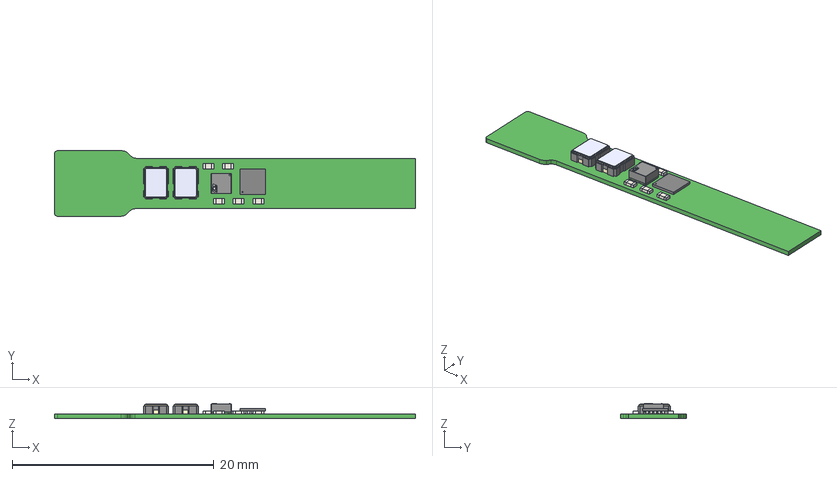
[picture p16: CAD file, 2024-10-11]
TEG_harvester_battery_free/hardware/Dental Sensor V110 - CAP/Generated Output/Dental Sensor - CAP.step
35.8 x 6.50 x 1.44 mm
CPH3225A--3DModel-STEP-56544 x 2
base
logo
terminals
Extruded x 15
WLCSP25_SOT1401-1_NXP

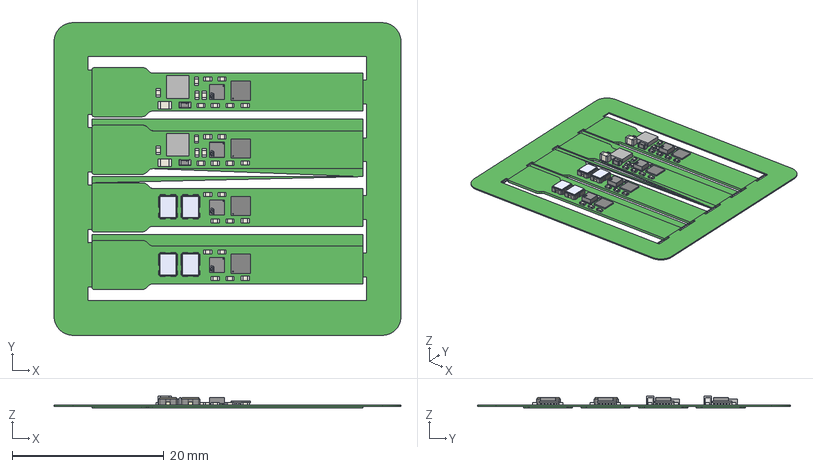
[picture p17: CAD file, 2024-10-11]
TEG_harvester_battery_free/hardware/Dental Sensor V110 - Panel/Generated Output/Dental Sensor - Panel.step
45.8 x 41.3 x 1.64 mm
Extruded x 98
base x 4
logo x 4
terminals x 4
TDK Logo x 2
WLCSP25_SOT1401-1_NXP x 4
CPH3225A--3DModel-STEP-56544 x 4

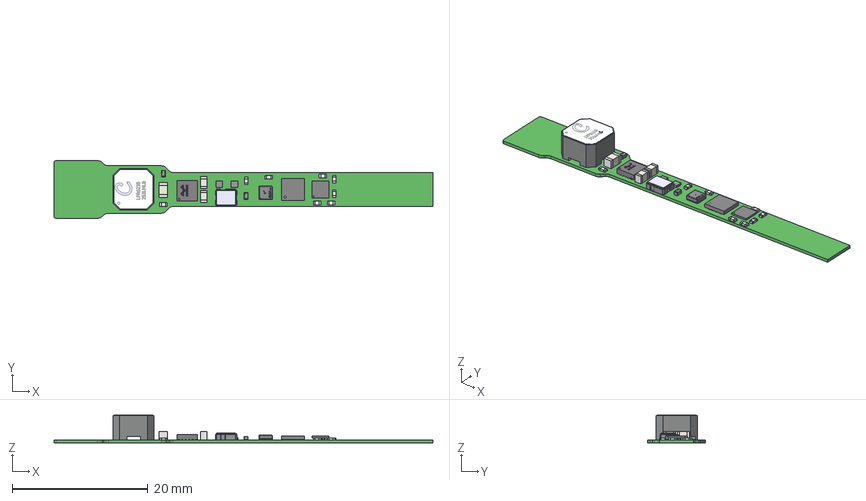
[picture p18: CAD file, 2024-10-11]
TEG_harvester_battery_free/hardware/Dental Sensor V400/Generated Output/Dental Sensor - V400.step
55.8 x 8.50 x 4.07 mm
MOLD-SNB04A x 2
FRAME-SNB04A x 2
8-GQFN v8
Extruded x 33
CPH3225A--3DModel-STEP-56544
Pins x 2
Band x 2
Diodes_Logo x 2
Trans_Coilcraft_LPR6235-253LMLB_eec
MCRY12-DFN10
WLCSP25_SOT1401-1_NXP
STM Logo

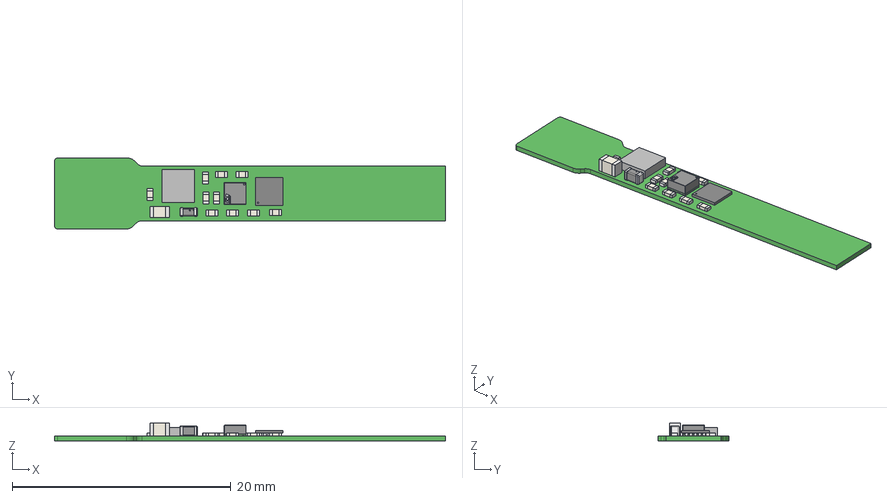
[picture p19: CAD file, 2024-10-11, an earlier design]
TEG_harvester_battery_free/hardware/Dental Sensor V110/Dental Sensor.step
35.8 x 6.50 x 1.64 mm
Extruded x 34
base
logo
terminals
TDK Logo
WLCSP25_SOT1401-1_NXP

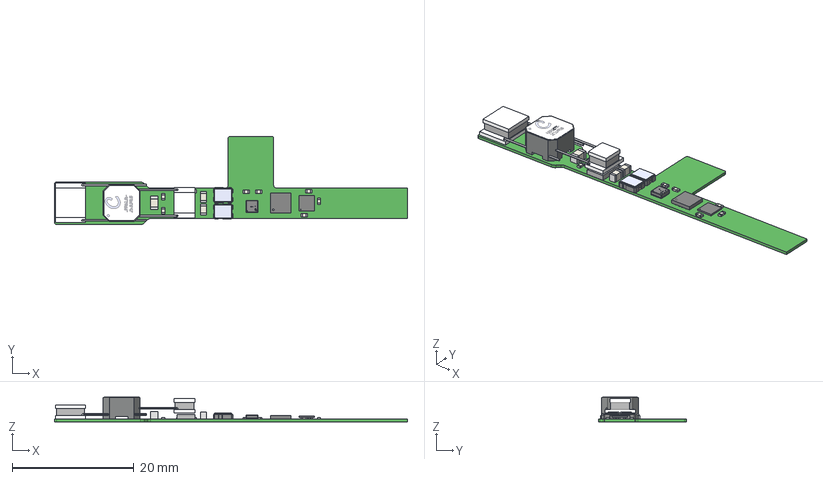
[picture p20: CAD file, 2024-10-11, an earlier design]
TEG_harvester_battery_free/hardware/Dental Sensor V200/Generated Output/Dental Sensor - V200.step
58.0 x 14.5 x 4.07 mm
Extruded x 37
Trans_Coilcraft_LPR6235-253LMLB_eec
CPH3225A--3DModel-STEP-56544 x 2
8-GQFN v8
WLCSP25_SOT1401-1_NXP
STM Logo
CUI_DEVICES_CP074965-239
CUI_DEVICES_CP073450-238

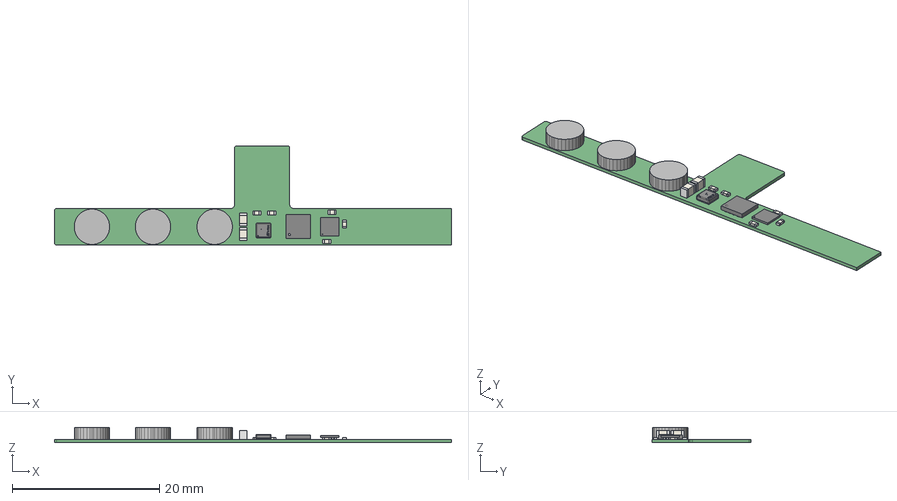
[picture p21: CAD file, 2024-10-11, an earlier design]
TEG_harvester_battery_free/hardware/Dental Sensor V300/Generated Output/Dental Sensor - V300.step
54.0 x 13.5 x 2.09 mm
Extruded x 24
8-GQFN v8
WLCSP25_SOT1401-1_NXP
STM Logo

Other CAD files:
TEG_harvester_battery_free/hardware/Dental Sensor V110/Generated Output/Dental Sensor.step

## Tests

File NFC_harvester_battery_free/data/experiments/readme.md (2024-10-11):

# Data - Experiments
All scripts and data used for the machine learning experiments.

## Folders

### data_dumps
Folder containing the raw data obtained from the densor for this experiment.

### experiment_protocols
Folder containing the protocols used during the experiments. Can be loaded in experiment_master_ui.py.

### labeled_data
Folder containing CSV files with labeled data from the Densor

### labeled_data_ear_mouth
Folder containing CSV files with labeled data from the ear-mounted accelerometer.

### plots
Folder where plots generated by scripts in the data/experiments folder are stored.

## Files

### data_labeler.py
File containing methods to label data generated by the Densor and the ear-mounted accelerometer. Uses the index.json file to find the corresponding protocol.

### data_master.py
Script used to label Densor and ear-mounted accelerometer data.

### data_ml.py
Program that handles all machine learning on Densor data.

### data_process_apple_watch_dumps.py
Script to convert an Apple healthkit export into a protocol that can be used to label Densor data.

### data_stats.py
Script that holds methods for plotting machine learning related plots.

### earpiece_ml.py
Program that handles all machine learning on ear-mounted accelerometer data.

### experiment_master_ui.py
User interface for a program used to run experiments. Randomizes tasks, displays them to the user, gives a timer for every task and saves protocols to the index file after running.

### experiment_master.py
Background methods and command-line version of program controlling the experiments. Randomizes tasks, displays them to the user, gives a timer for every task and saves protocols to the index file after running.

### index.json
JSON file containing all data (including the protocol used) for every dataset in the data_dumps and labeled_data folder.

### plot_labeled.py
Program to plot labeled Densor data.

### plot_ear_mouth_example_trace.py
Program to plot an example trace of all sensors used in the comparison between ear and mouth experiment. Different traces can be generated by using the arguments "--mimu" for the Densor accelerometer trace, "-mpd" for the Densor photo-diode trace and "--ear" for the ear-mounted accelerometer trace.

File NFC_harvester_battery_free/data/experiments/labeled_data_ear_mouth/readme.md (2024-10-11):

# labeled_data_ear_mouth
All labeled data from the ear-piece of the comparison between an ear mounted accelerometer and the Densor.

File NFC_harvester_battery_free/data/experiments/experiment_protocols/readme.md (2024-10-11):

# Experiment protocols
Protocols used to determine which steps to undertake while performing experiments with the densor. A description per protocol can be found below
## all_examples_v1.json
Combination of all possible tasks. Made to be excluded from machine learning models.
## all_examples_v2.json
Combination of all possible tasks including head rotation while laying. Made to be excluded from machine learning models.
## ear_mouth_v1.json
Only opening and closing the mouth repeaditly. Made to be seperable from other experiments containing mouth open and close events.
## grinding_v1.json
Repeaditly grind and not grind teeth.
## not_wearing_v1.json
Created to collect data where the Densor in not worn. Used for orthodontic compliance classification.
## open_close_speak_drink_v1.json
Main protocol used for most experiments. Wear with mouth opened and closed, speaking and drinking events.
## rotation_v1.json
Used to verify rotation readings and calculation from the accelerometer. Made to be excluded from machine learning models.
## sleeping_v1.json
Used to detect head rotation while sleeping.

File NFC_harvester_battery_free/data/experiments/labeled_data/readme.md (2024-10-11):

# labeled_data
All labeled data from the Densor, used in the machine learning models.

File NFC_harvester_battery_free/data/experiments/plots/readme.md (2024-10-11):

# data - experiments - plots
Folder where all plots, generated by scripts at the top level, are being stored.

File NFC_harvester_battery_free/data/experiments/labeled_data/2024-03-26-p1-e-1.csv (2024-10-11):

label | m_temp | m_pd | m_accel_x | m_accel_y | m_accel_z | m_vdda
Get ready | 24.0475 | 1716.825396825397 | 4124 | 15468 | -1840 | 2.6
Get ready | 24.235 | 1558.7301587301588 | -7468 | 3888 | -9268 | 2.6
Get ready | 24.235 | 1147.3015873015872 | -580 | -996 | -22648 | 2.6
Get ready | 24.0475 | 1036.1904761904761 | -2688 | 320 | -16392 | 2.6
Get ready | 24.36 | 1126.984126984127 | -5288 | -5276 | -27680 | 2.6
Get ready | 24.4375 | 1574.4810744810745 | 16348 | -2020 | -1776 | 2.5
Get ready | 24.5 | 1231.3797313797313 | 20084 | 8480 | -22272 | 2.5
Get ready | 24.375 | 1575.7020757020757 | -24036 | -7032 | -12648 | 2.5
Get ready | 25.1875 | 526.2515262515262 | 16432 | -1040 | -1328 | 2.5
Get ready | 27.25 | 567.7655677655678 | 15668 | -464 | 2080 | 2.5
Get ready | 28.75 | 657.5091575091575 | 16440 | -1912 | 1732 | 2.5
Get ready | 29.6875 | 527.4725274725274 | 16016 | -672 | 1600 | 2.5
Get ready | 30.375 | 532.967032967033 | 16776 | -440 | 856 | 2.5
Get ready | 30.5625 | 509.7680097680098 | 15488 | -1756 | 1696 | 2.5
Get ready | 31.1875 | 533.5775335775336 | 17304 | -1240 | 1920 | 2.5
Get ready | 31.375 | 605.006105006105 | 17424 | -7964 | -876 | 2.5
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

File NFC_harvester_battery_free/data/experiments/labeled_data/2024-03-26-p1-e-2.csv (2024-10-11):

label | m_temp | m_pd | m_accel_x | m_accel_y | m_accel_z | m_vdda
Get ready | 21.985 | 1187.3015873015872 | -11892 | 10436 | 4036 | 2.6
Get ready | 22.11 | 1528.888888888889 | 6272 | 17036 | -800 | 2.6
Get ready | 22.235 | 1017.1428571428571 | -7128 | -9668 | -20056 | 2.6
Get ready | 22.25 | 1401.7094017094016 | 13216 | -4552 | 3180 | 2.5
Get ready | 24.4225 | 538.4126984126984 | 16720 | -3120 | 340 | 2.6
Get ready | 26.735 | 528.2539682539684 | 15960 | 160 | -404 | 2.6
Get ready | 28.61 | 659.047619047619 | 16332 | -936 | 2144 | 2.6
Get ready | 29.7975 | 532.6984126984127 | 16184 | -724 | 2504 | 2.6
Get ready | 30.5475 | 518.0952380952381 | 16444 | -668 | 2784 | 2.6
Get ready | 30.86 | 568.8888888888889 | 16468 | 512 | -468 | 2.6
Get ready | 31.4225 | 563.8095238095239 | 14132 | -1984 | -456 | 2.6
Get ready | 31.7975 | 556.825396825397 | 16136 | -3076 | -712 | 2.6
Get ready | 32.1875 | 527.4725274725274 | 16164 | -1172 | 644 | 2.5
Get ready | 32.5625 | 656.2881562881563 | 16516 | 300 | 848 | 2.5
Get ready | 32.5 | 513.4310134310134 | 15864 | -4944 | -440 | 2.5
Get ready | 32.625 | 492.6739926739927 | 15320 | -1864 | 288 | 2.5
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

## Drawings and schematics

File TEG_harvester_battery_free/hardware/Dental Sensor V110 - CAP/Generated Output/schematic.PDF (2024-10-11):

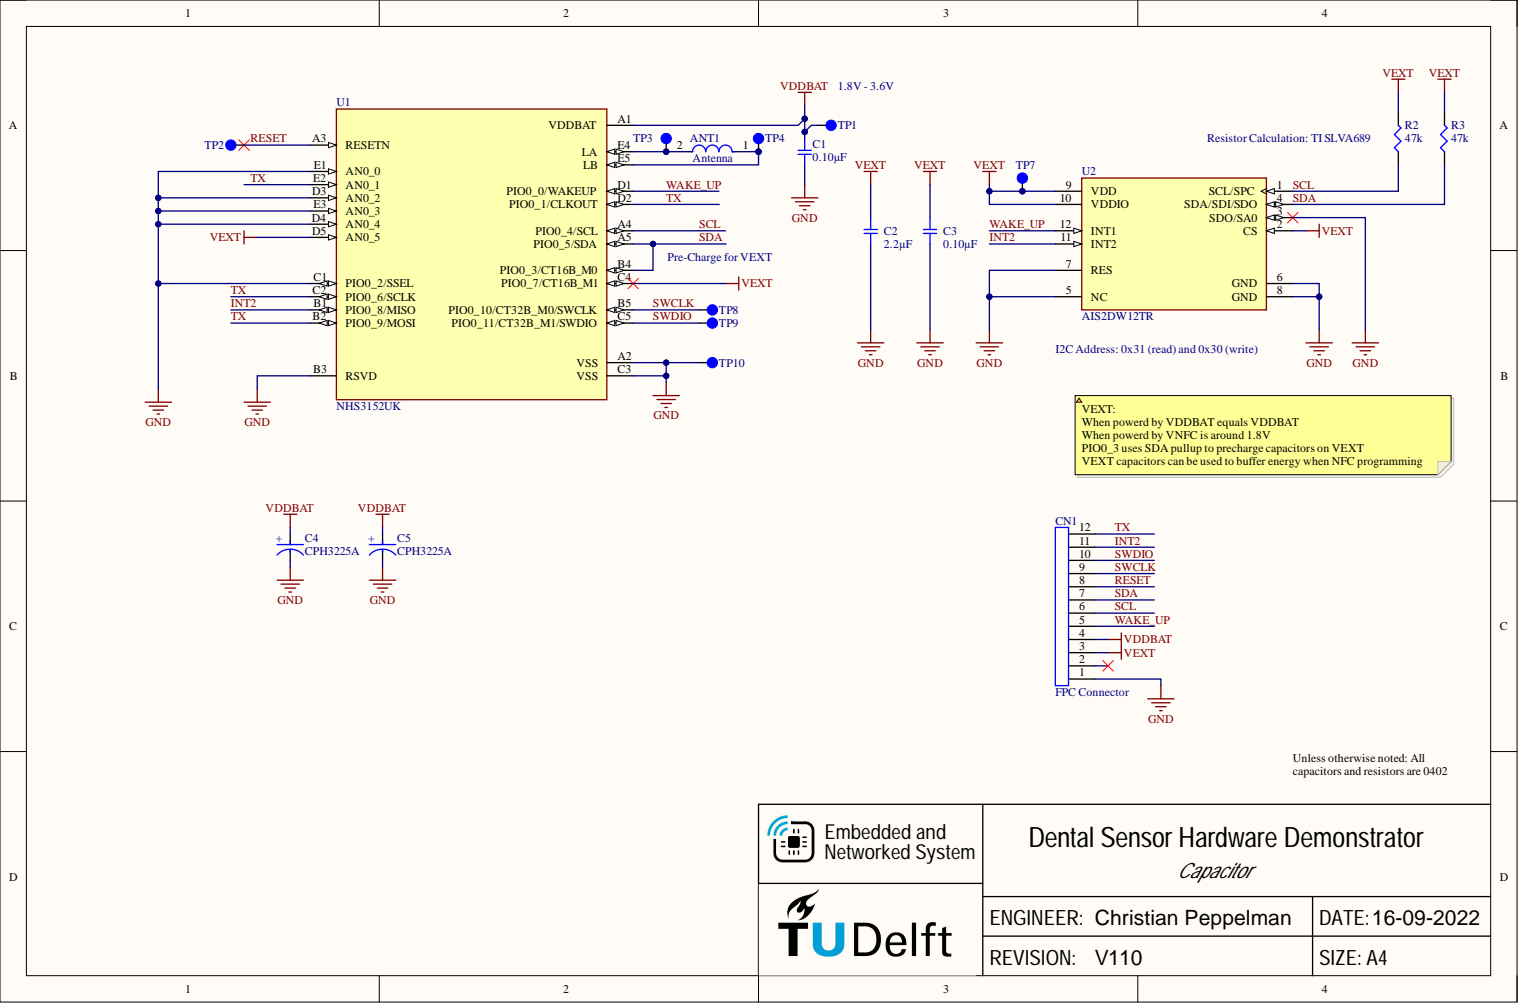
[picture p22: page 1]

E 5 | A n ten n a

SCL

E 3
D 4

Dental Sensor Hardware Demonstrator

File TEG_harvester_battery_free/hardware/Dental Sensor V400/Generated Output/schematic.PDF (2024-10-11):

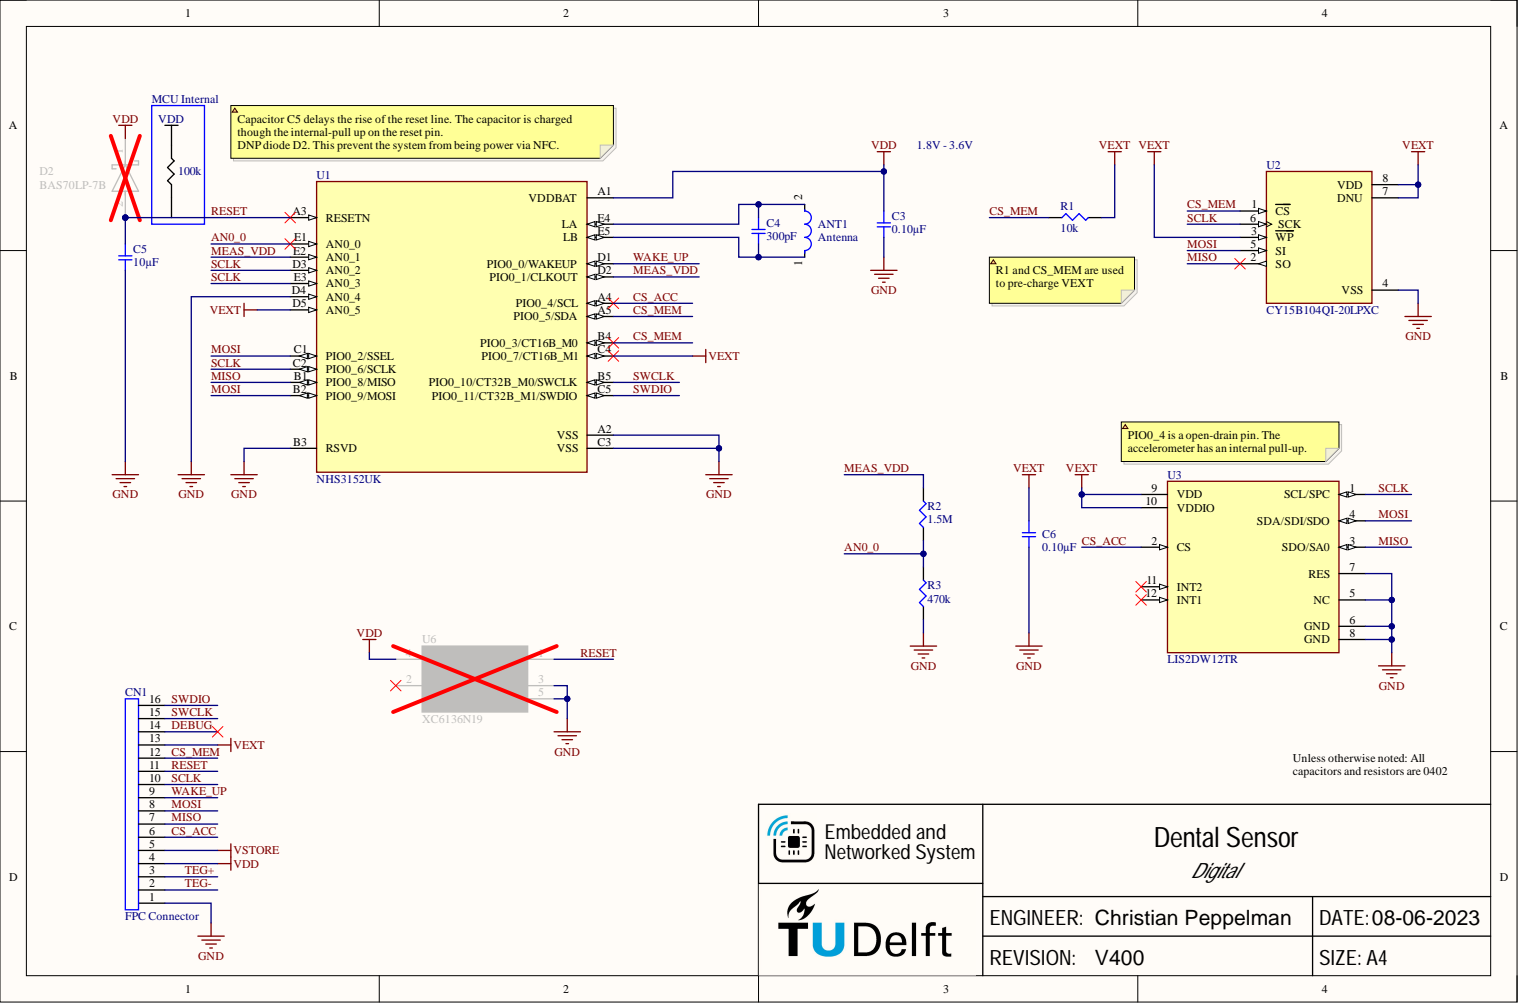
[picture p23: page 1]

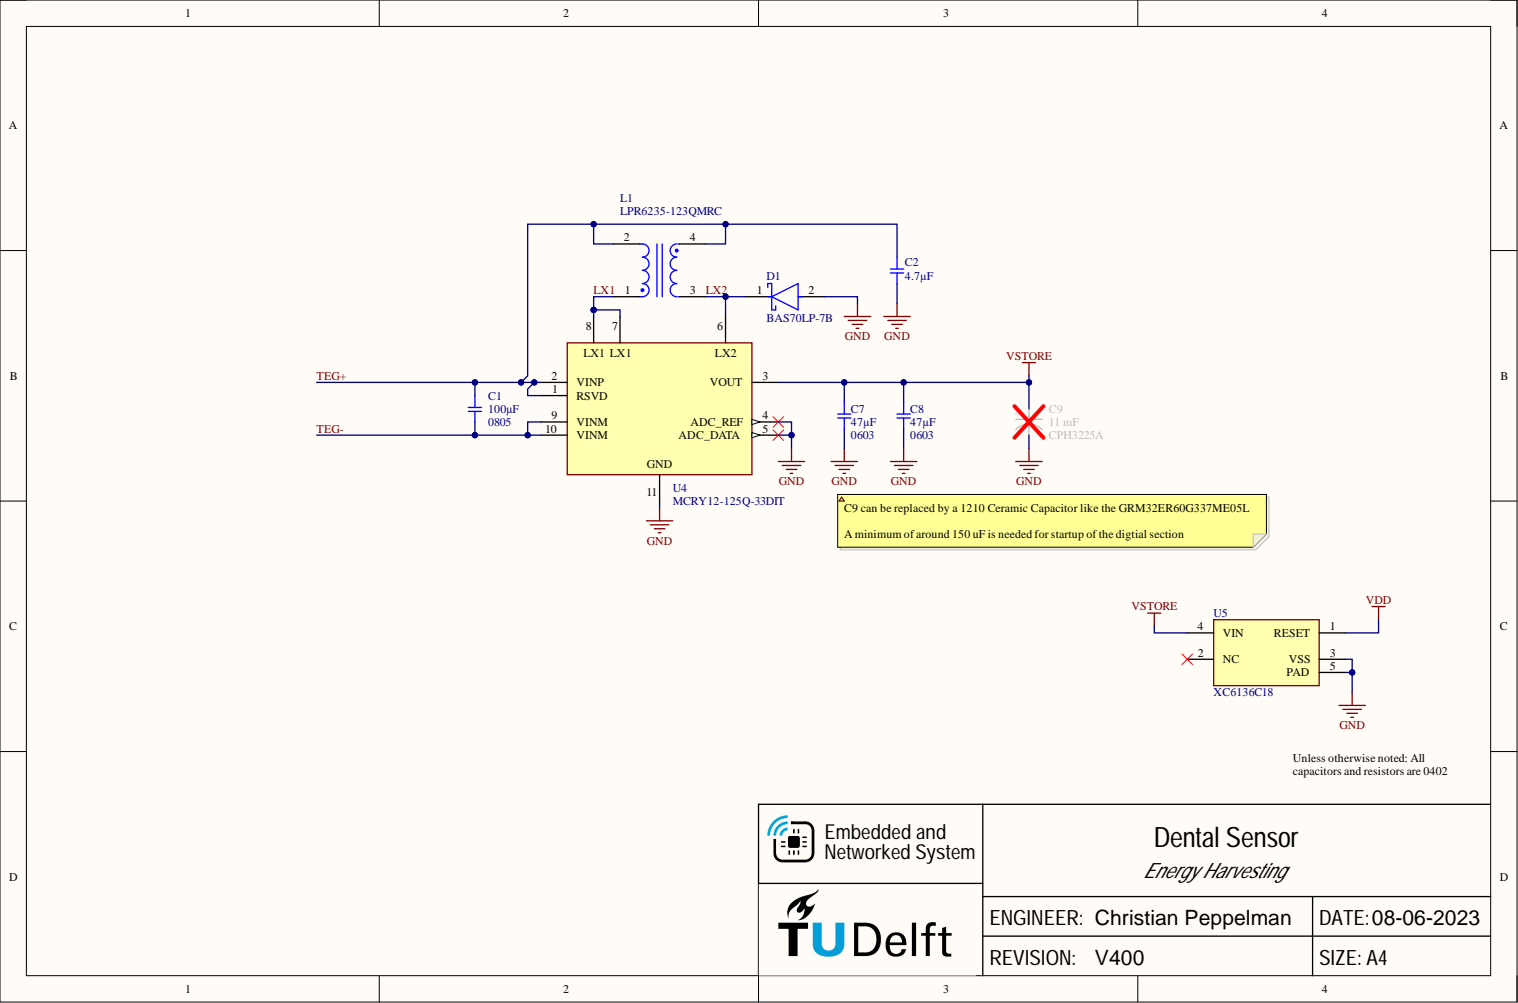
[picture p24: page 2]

C9 can be replaced by a 1210 Ceramic Capacitor like the GRM32ER60G337ME05L

A minimum of around 150 uF is needed for startup of the digtialsection

Unless otherwise noted: All
capacitors and resistors are 0402

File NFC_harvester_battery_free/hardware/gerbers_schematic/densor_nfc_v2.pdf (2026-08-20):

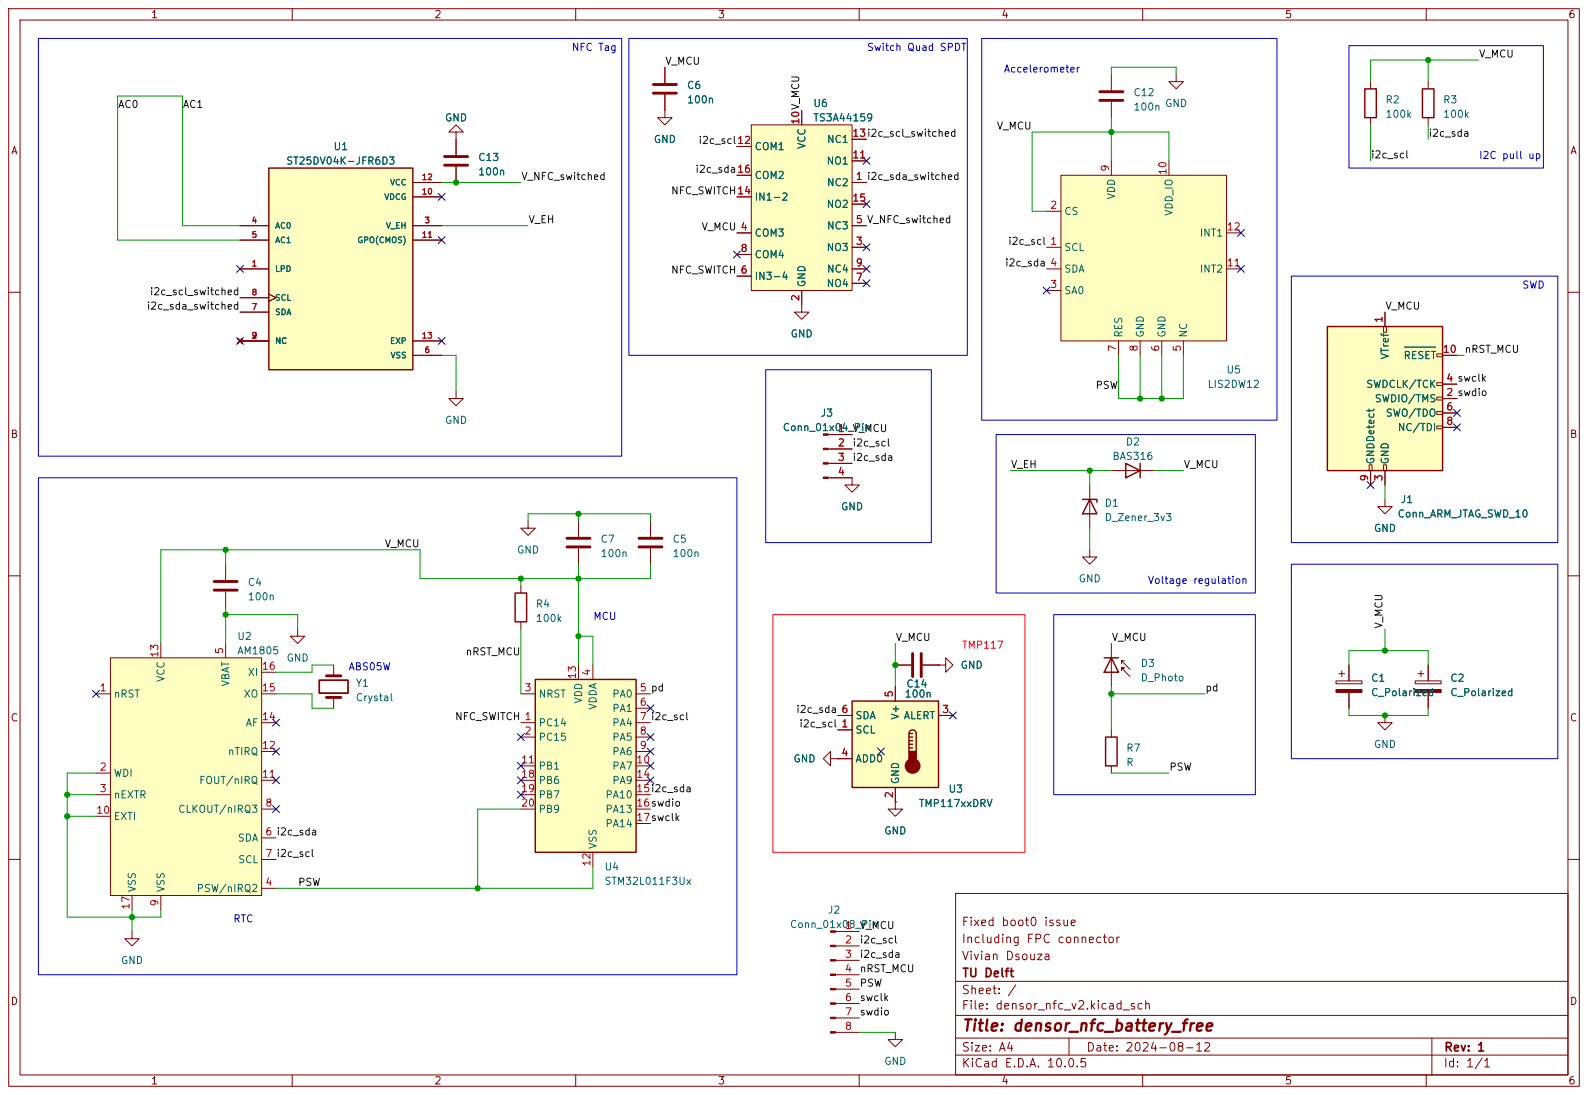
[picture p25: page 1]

SWD NFC Tag MCU

Size: A4 | Rev: 1
KiCad E.D.A. 10.0.5 | Id: 1/1

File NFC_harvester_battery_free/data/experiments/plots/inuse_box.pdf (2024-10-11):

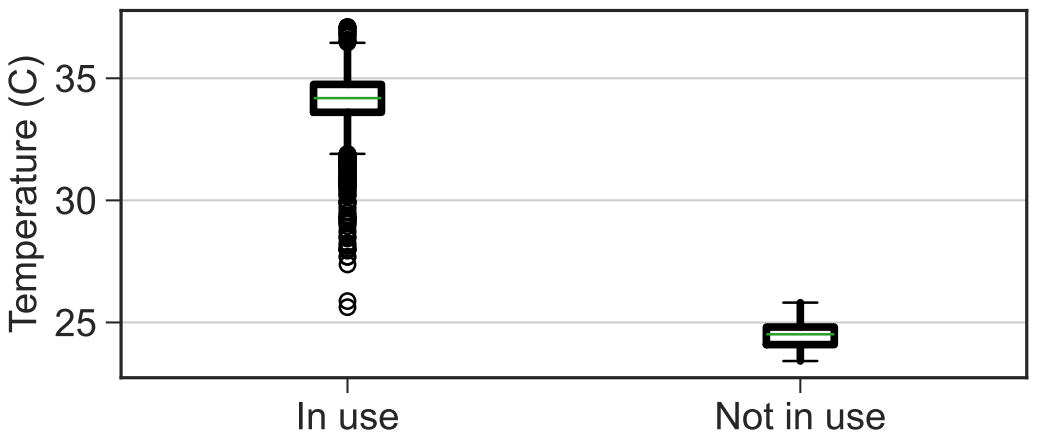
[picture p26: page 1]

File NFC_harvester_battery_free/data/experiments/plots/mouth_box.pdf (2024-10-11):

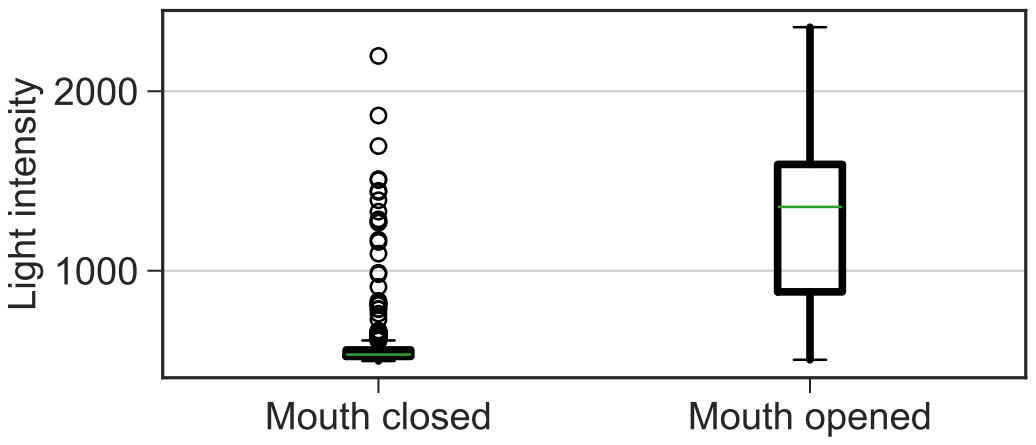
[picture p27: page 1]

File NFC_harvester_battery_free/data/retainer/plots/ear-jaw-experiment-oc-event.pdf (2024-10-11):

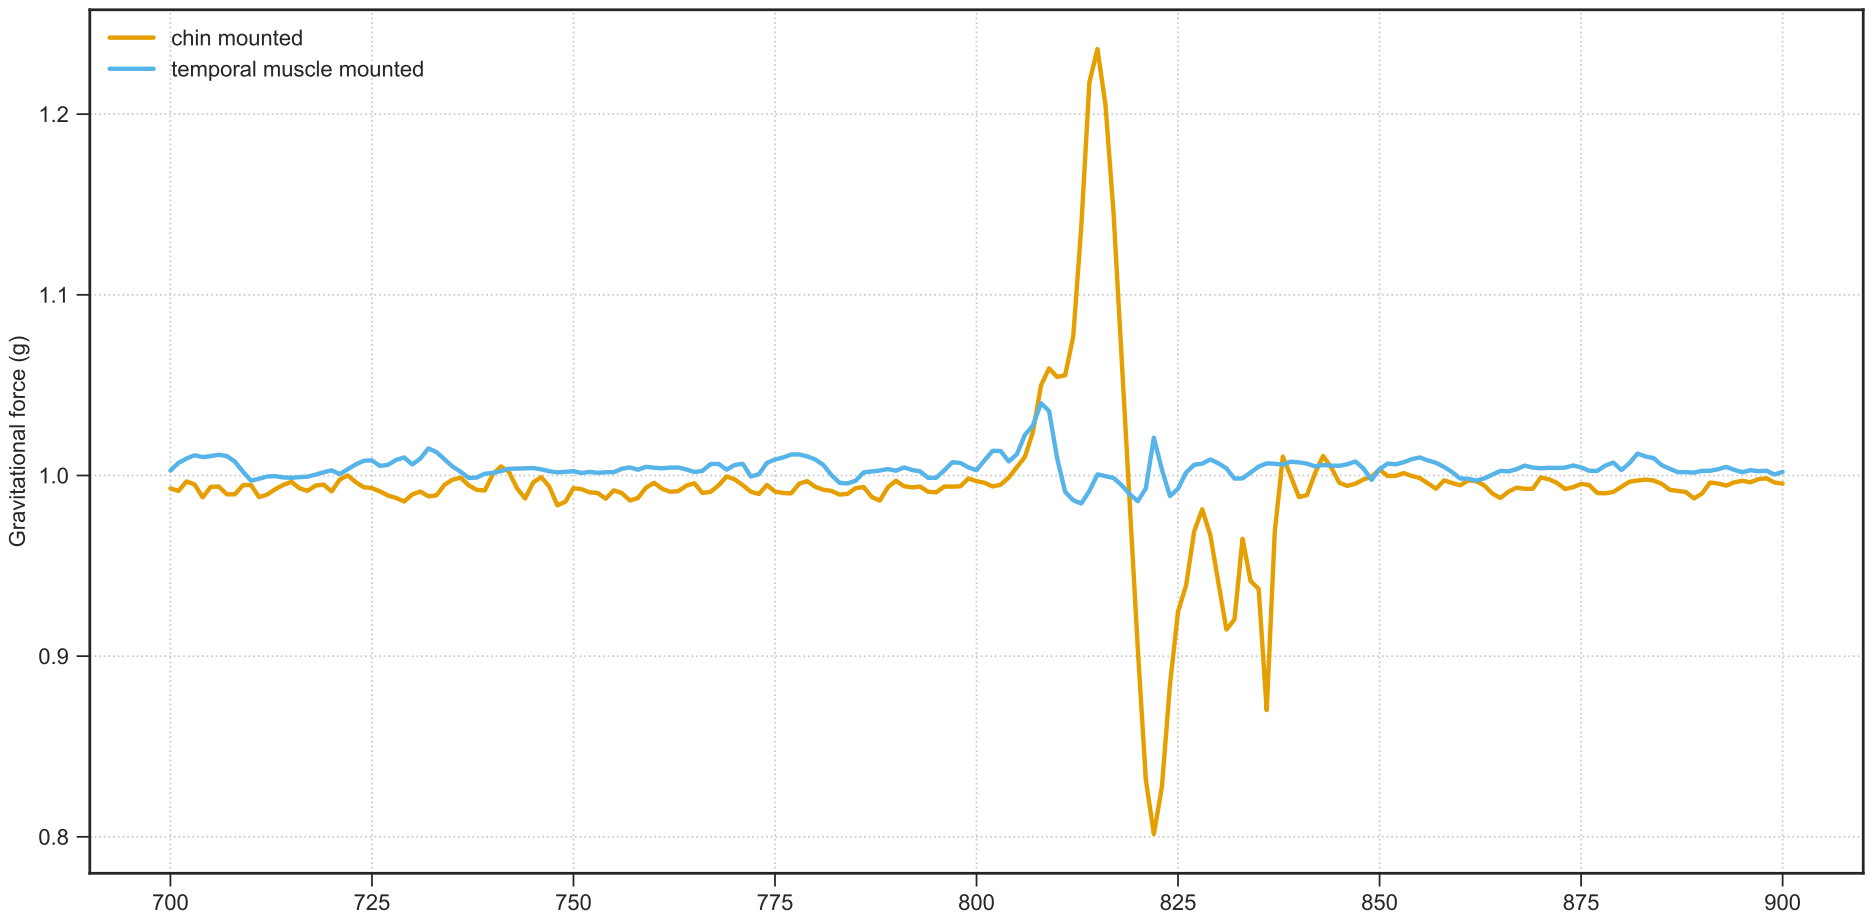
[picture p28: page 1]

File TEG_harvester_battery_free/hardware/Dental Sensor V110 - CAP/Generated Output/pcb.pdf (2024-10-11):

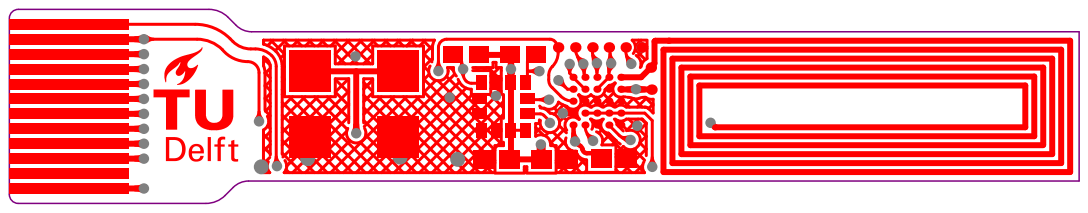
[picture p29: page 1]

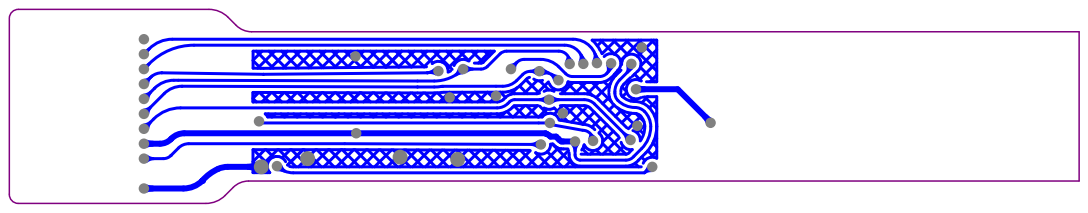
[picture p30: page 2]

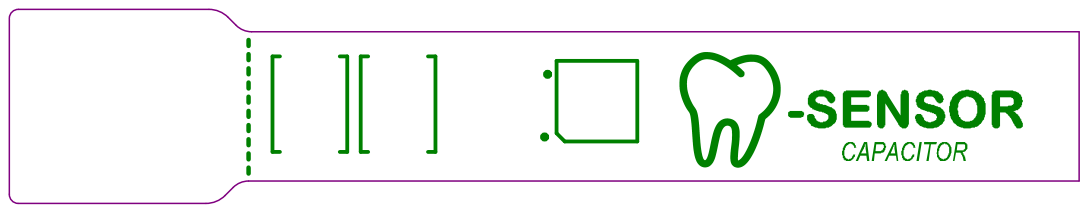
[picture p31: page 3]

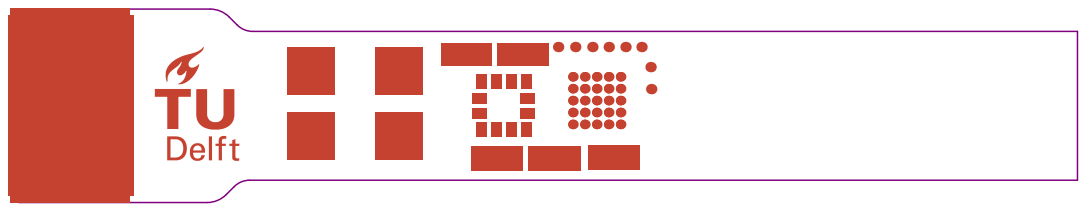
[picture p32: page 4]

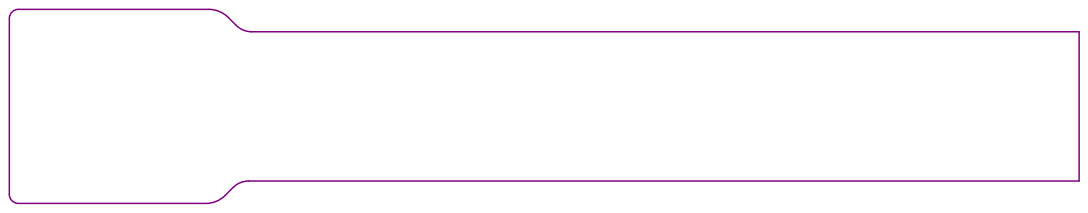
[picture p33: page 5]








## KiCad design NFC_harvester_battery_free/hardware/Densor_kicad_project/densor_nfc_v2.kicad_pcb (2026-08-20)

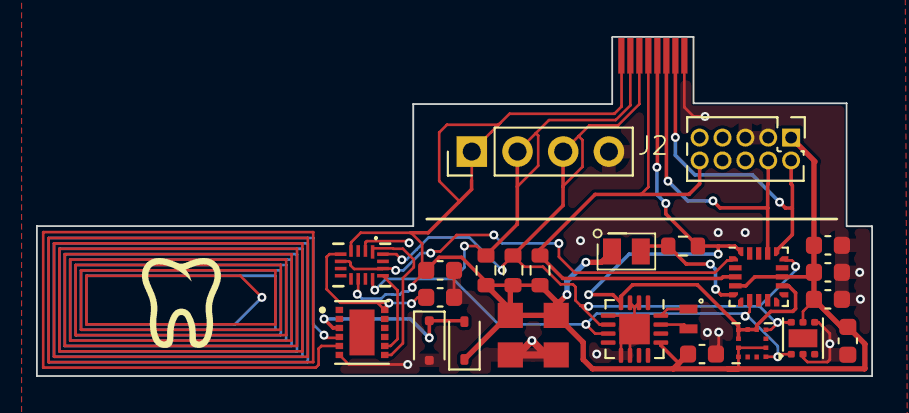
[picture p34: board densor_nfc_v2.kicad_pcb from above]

Board: 2 copper layers, 46.4 x 18.8 mm, 26 parts (0 on the bottom side), 17 nets.

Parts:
C1, C2: C_Polarized; CPX3225A
C4, C5, C6, C7, C12, C13, C14: 100n; C_0603_1608Metric
D1: D_Zener_3v3; D_SOD-323F
D2: BAS316; D_SOD-323
D3: D_Photo; pd_vemd1060x01
J1: Conn_ARM_JTAG_SWD_10; PinHeader_2x05_P1.27mm_Vertical
J2: Conn_01x08_Pin; fpc_503480-0800
J3: Conn_01x04_Pin; PinHeader_1x04_P2.54mm_Vertical
R2, R3, R4: 100k; R_0603_1608Metric
R7: R; R_0603_1608Metric
U1: ST25DV04K-JFR6D3; PSON50P300X300X60-13N
U2: AM1805; QFN-16-1EP_3x3mm_P0.5mm_EP1.7x1.7mm
U3: TMP117xxDRV; WSON-6-1EP_2x2mm_P0.65mm_EP1x1.6mm
U4: STM32L011F3Ux; ST_UFQFPN-20_3x3mm_P0.5mm
U5: LIS2DW12; Kionix_LGA-12_2x2mm_P0.5mm_LayoutBorder2x4y
U6: TS3A44159; RSV16
Y1: Crystal; ABS05W_Crystal

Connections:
/AC0: U1.4 (AC0), U1.5 (AC1)
/NFC_SWITCH: U4.1 (PC14), U6.6 (IN3-4), U6.14 (IN1-2)
/PSW: J2.5, R7.2, U2.4 (PSW/nIRQ2), U4.12 (VSS), U4.20 (PB9), U5.5 (NC), U5.6 (GND), U5.7 (RES), U5.8 (GND)
/V_EH: D1.1 (K), D2.2 (A), U1.3 (V_EH)
/V_MCU: C1.1, C2.1, C4.1, C5.2, C6.1, C7.2, C12.2, C14.2, D2.1 (K), D3.1 (K), J1.1 (VTref), J2.1, J3.1, R2.1, R3.1, R4.1, U2.13 (VCC), U3.5 (V+), U4.4 (VDDA), U4.13 (VDD), U5.2 (CS), U5.9 (VDD), U5.10 (VDD_IO), U6.4 (COM3), U6.10 (VCC)
/V_NFC_switched: C13.2, U1.12 (VCC), U6.5 (NC3)
/i2c_scl: J2.2, J3.2, R2.2, U2.7 (SCL), U3.1 (SCL), U4.7 (PA4), U5.1 (SCL), U6.12 (COM1)
/i2c_scl_switched: U1.8 (SCL), U6.13 (NC1)
/i2c_sda: J2.3, J3.3, R3.2, U2.6 (SDA), U3.6 (SDA), U4.15 (PA10), U5.4 (SDA), U6.16 (COM2)
/i2c_sda_switched: U1.7 (SDA), U6.1 (NC2)
/nRST_MCU: J1.10 (~RESET), J2.4, R4.2, U4.3 (NRST)
/pd: D3.2 (A), R7.1, U4.5 (PA0)
/swclk: J1.4 (SWDCLK/TCK), J2.6, U4.17 (PA14)
/swdio: J1.2 (SWDIO/TMS), J2.7, U4.16 (PA13)
GND: C1.2, C2.2, C4.2, C5.1, C6.2, C7.1, C12.1, C13.1, C14.1, D1.2 (A), J1.3 (GND), J1.5 (GND), J2.8, J3.4, U1.6 (VSS), U2.2 (WDI), U2.3 (nEXTR), U2.5 (VBAT), U2.9 (VSS), U2.10 (EXTI), U2.17 (VSS), U3.2 (GND), U3.4 (ADD0), U6.2 (GND)
unnamed: U2.16 (XI), Y1.1
unnamed: U2.15 (XO), Y1.2

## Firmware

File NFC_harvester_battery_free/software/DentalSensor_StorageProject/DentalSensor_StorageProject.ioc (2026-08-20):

#MicroXplorer Configuration settings - do not modify
ADC.ContinuousConvMode=DISABLE
ADC.DiscontinuousConvMode=ENABLE
ADC.IPParameters=ContinuousConvMode,DiscontinuousConvMode
CAD.formats=
CAD.pinconfig=
CAD.provider=
File.Version=6
GPIO.groupedBy=Group By Peripherals
I2C1.I2C_Speed_Mode=I2C_Standard
I2C1.IPParameters=I2C_Speed_Mode
KeepUserPlacement=false
Mcu.CPN=STM32L021F4U6TR
Mcu.Family=STM32L0
Mcu.IP0=ADC
Mcu.IP1=I2C1
Mcu.IP2=NVIC
Mcu.IP3=RCC
Mcu.IP4=SYS
Mcu.IPNb=5
Mcu.Name=STM32L021F4Ux
Mcu.Package=UFQFPN20
Mcu.Pin0=PC14-OSC32_IN
Mcu.Pin1=PA0-CK_IN
Mcu.Pin2=PA1
Mcu.Pin3=PA4
Mcu.Pin4=PA10
Mcu.Pin5=PA13
Mcu.Pin6=PA14
Mcu.Pin7=VP_ADC_Vref_Input
Mcu.PinsNb=8
Mcu.ThirdPartyNb=0
Mcu.UserConstants=
Mcu.UserName=STM32L021F4Ux
MxCube.Version=6.9.2
MxDb.Version=DB.6.0.92
NVIC.ForceEnableDMAVector=true
NVIC.HardFault_IRQn=true\:0\:0\:false\:false\:true\:false\:false\:false
NVIC.NonMaskableInt_IRQn=true\:0\:0\:false\:false\:true\:false\:false\:false
NVIC.PendSV_IRQn=true\:0\:0\:false\:false\:true\:false\:false\:false
NVIC.SVC_IRQn=true\:0\:0\:false\:false\:true\:false\:false\:true
NVIC.SysTick_IRQn=true\:3\:0\:false\:false\:true\:false\:true\:false
PA0-CK_IN.GPIOParameters=GPIO_Label
PA0-CK_IN.GPIO_Label=pd
PA0-CK_IN.Locked=true
PA0-CK_IN.Mode=IN0
PA0-CK_IN.Signal=ADC_IN0
PA1.GPIOParameters=GPIO_Label
PA1.GPIO_Label=moisture
PA1.Locked=true
PA1.Signal=ADC_IN1
PA10.GPIOParameters=GPIO_Pu
PA10.GPIO_Pu=GPIO_NOPULL
PA10.Mode=I2C
PA10.Signal=I2C1_SDA
PA13.Locked=true
PA13.Mode=Serial_Wire
PA13.Signal=SYS_SWDIO
PA14.Mode=Serial_Wire
PA14.Signal=SYS_SWCLK
PA4.GPIOParameters=GPIO_Pu
PA4.GPIO_Pu=GPIO_NOPULL
PA4.Mode=I2C
PA4.Signal=I2C1_SCL
PC14-OSC32_IN.GPIOParameters=PinState,GPIO_Label
PC14-OSC32_IN.GPIO_Label=NFC_SWITCH
PC14-OSC32_IN.Locked=true
PC14-OSC32_IN.PinState=GPIO_PIN_RESET
PC14-OSC32_IN.Signal=GPIO_Output
PinOutPanel.RotationAngle=0
ProjectManager.AskForMigrate=true
ProjectManager.BackupPrevious=false
ProjectManager.CompilerLinker=GCC
ProjectManager.CompilerOptimize=6
ProjectManager.ComputerToolchain=false
ProjectManager.CoupleFile=false
ProjectManager.CustomerFirmwarePackage=
ProjectManager.DefaultFWLocation=true
ProjectManager.DeletePrevious=true
ProjectManager.DeviceId=STM32L021F4Ux
ProjectManager.FirmwarePackage=STM32Cube FW_L0 V1.12.2
ProjectManager.FreePins=false
ProjectManager.HalAssertFull=false
ProjectManager.HeapSize=0x200
ProjectManager.KeepUserCode=true
ProjectManager.LastFirmware=true
ProjectManager.LibraryCopy=1
ProjectManager.MainLocation=Core/Src
ProjectManager.NoMain=false
ProjectManager.PreviousToolchain=
ProjectManager.ProjectBuild=false
ProjectManager.ProjectFileName=DentalSensor_StorageProject.ioc
ProjectManager.ProjectName=DentalSensor_StorageProject
ProjectManager.ProjectStructure=
ProjectManager.RegisterCallBack=
ProjectManager.StackSize=0x400
ProjectManager.TargetToolchain=STM32CubeIDE
ProjectManager.ToolChainLocation=
ProjectManager.UAScriptAfterPath=
ProjectManager.UAScriptBeforePath=
ProjectManager.UnderRoot=true
ProjectManager.functionlistsort=1-SystemClock_Config-RCC-false-HAL-false,2-MX_GPIO_Init-GPIO-false-HAL-true,3-MX_I2C1_Init-I2C1-false-HAL-true,4-MX_ADC_Init-ADC-false-HAL-true
RCC.AHBFreq_Value=2097000
RCC.APB1Freq_Value=2097000
RCC.APB1TimFreq_Value=2097000
RCC.APB2Freq_Value=2097000
RCC.APB2TimFreq_Value=2097000
RCC.FCLKCortexFreq_Value=2097000
RCC.FamilyName=M
RCC.HCLKFreq_Value=2097000
RCC.HSE_VALUE=8000000
RCC.HSI16_VALUE=16000000
RCC.HSI_VALUE=16000000
RCC.I2C1Freq_Value=2097000
RCC.I2c1ClockSelection=RCC_I2C1CLKSOURCE_SYSCLK
RCC.IPParameters=AHBFreq_Value,APB1Freq_Value,APB1TimFreq_Value,APB2Freq_Value,APB2TimFreq_Value,FCLKCortexFreq_Value,FamilyName,HCLKFreq_Value,HSE_VALUE,HSI16_VALUE,HSI_VALUE,I2C1Freq_Value,I2c1ClockSelection,LPTIMFreq_Value,LPUARTFreq_Value,LSE_VALUE,LSI_VALUE,MCOPinFreq_Value,MSI_VALUE,PLLCLKFreq_Value,RTCFreq_Value,RTCHSEDivFreq_Value,SYSCLKFreq_VALUE,TIMFreq_Value,TimerFreq_Value,USART2Freq_Value,VCOOutputFreq_Value,WatchDogFreq_Value
RCC.LPTIMFreq_Value=2097000
RCC.LPUARTFreq_Value=2097000
RCC.LSE_VALUE=32768
RCC.LSI_VALUE=37000
RCC.MCOPinFreq_Value=2097000
RCC.MSI_VALUE=2097000
RCC.PLLCLKFreq_Value=24000000
RCC.RTCFreq_Value=37000
RCC.RTCHSEDivFreq_Value=4000000
RCC.SYSCLKFreq_VALUE=2097000
RCC.TIMFreq_Value=2097000
RCC.TimerFreq_Value=2097000
RCC.USART2Freq_Value=2097000
RCC.VCOOutputFreq_Value=48000000
RCC.WatchDogFreq_Value=37000
VP_ADC_Vref_Input.Mode=IN-Vrefint
VP_ADC_Vref_Input.Signal=ADC_Vref_Input
board=custom
isbadioc=false

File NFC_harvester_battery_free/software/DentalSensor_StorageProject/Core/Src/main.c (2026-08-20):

/* USER CODE BEGIN Header */
/**
  ******************************************************************************
  * @file           : main.c
  * @brief          : Firmware for the Densor project.
  ******************************************************************************
  */
/* USER CODE END Header */
/* Includes ------------------------------------------------------------------*/
#include "main.h"

/* Private includes ----------------------------------------------------------*/
/* USER CODE BEGIN Includes */
#include <stdbool.h>
#include "tmp117.h"

/* USER CODE END Includes */

/* Private typedef -----------------------------------------------------------*/
/* USER CODE BEGIN PTD */

/* USER CODE END PTD */

/* Private define ------------------------------------------------------------*/
/* USER CODE BEGIN PD */
#define NFC_ADDR 					0xA6
#define ACCEL_ADDR 					0x32
#define DEBUG_TERMINAL				0xAA
#define AM1805_ADDR 				0xD2

#define ACCEL_TEMP_BASE				0x0D
#define ACCEL_CONTROL1				0x20
#define ACCEL_OUT_X_L				0x28

#define RTC_SECONDS                 0x01
#define RTC_SECONDS_ALARM           0x09
#define RTC_MINUTES					0x02
#define RTC_MINUTES_ALARM			0x0A
#define RTC_OSCILLATOR_CONTROL      0x1C
#define RTC_CONFIGURATION_KEY       0x1F
#define RTC_CONTROL2                0x11
#define RTC_INTMASK                 0x12
#define RTC_COUNTDOWN_TIMER_CONTROL 0x18
#define RTC_STATUS                  0x0F
#define RTC_SLEEP_CONTROL			0x17

#define SENSOR_ENABLE_REG			0x00
#define TIMESTAMP_REG				0x01
#define RTC_INTERVAL_REG			0x05
#define STARTUP_DELAY_REG			0x06
#define MEM_POINTER_REG				0x07

#define MEMORY_SIZE 				8192

#define VREF_CAL_ADDR				((uint16_t*) (0x1FF80078)) // Datasheet p.51
#define VREF_CAL_VDDA				3000 // Datasheet p.51

#define DEBUG_TEST 					false
#define CHARGE_MODE					true

/* ASSIGNMENT CODE BEGIN */
// used config for the firmware: 1 measurement and starts in shutdown mode
// gets put in one-shot mode upon need
// NB after testing we could up the AVG value if needed.
/**
 *  TMP117 CONFIG register
 *  changed values:
 *  	- MOD[1:0]: 00 -> 01 set to shutdown
 *  	- AVG[1:0]: 01 -> 00 set to no averaging
 *  to activate one-shot change MOD[1:0] to 11
 */
#define TMP117_DEFAULT_CONFIG 0b0000011000000000
#define TMP117_ONE_SHOT_BITS (0x03 << 5)
/* ASSIGNMENT CODE END */

/* USER CODE END PD */

/* Private macro -------------------------------------------------------------*/
/* USER CODE BEGIN PM */

/* USER CODE END PM */

/* Private variables ---------------------------------------------------------*/
ADC_HandleTypeDef hadc;

I2C_HandleTypeDef hi2c1;

/* USER CODE BEGIN PV */

// Pointer to current memory position to write to.
uint16_t memPointer = 9;
// Zero value. Used for wiping memory.
uint8_t zero = 0;
// Holder for the interval set on the RTC. Default is 10 seconds.
uint8_t rtcInterval = 0x10;

// Holder for the value in the seconds register on the RTC at boot.
uint8_t bootSeconds = 0x60;
// Holder for the value in the minutes register on the RTC at boot.
uint8_t bootMinutes = 0x60;
// Holder for the startup delay.
uint8_t startupDelay = 0x00;

// Holder for boolean that determines which clock source the RTC should use. If true uses internal RC clock, if false, uses external XT crystal.
bool rcEnable = true;
// Holders for booleans that determine which sensors are turned on and off.
bool tempEnable = false;
bool moistureEnable = false;
bool pdEnable = false;
bool accelEnable = false;

/* ASSIGNMENT CODE BEGIN */
// bool for sensorEnable of the TMP117
bool newTempEnable = false;
/* ASSIGNMENT CODE END */

/* USER CODE END PV */

/* Private function prototypes -----------------------------------------------*/
void SystemClock_Config(void);
static void MX_GPIO_Init(void);
static void MX_I2C1_Init(void);
static void MX_ADC_Init(void);
/* USER CODE BEGIN PFP */

/* USER CODE END PFP */

/* Private user code ---------------------------------------------------------*/
/* USER CODE BEGIN 0 */

/**
 * @brief  Overwrite of the _write function. Outputs all calls to _write on the I2C bus to the DEBUG_TERMINAL address. Returns the length of the string to write.
 *
 * @param file: File descriptor of file into which data is written.
 * @param ptr: Pointer to data to be written.
 * @param len: Length in bytes of data to be written.
 * @retval int
 */
int _write(int file, char *ptr, int len)
{
  (void)file;
  __attribute__((unused)) int DataIdx;

  HAL_I2C_Master_Transmit(&hi2c1, DEBUG_TERMINAL, (uint8_t *) ptr, len, HAL_MAX_DELAY);
  return len;
}

// Only set to true, will print debug characters to an external debugger on i2c address DEBUG_TERMINAL. Otherwise does nothing.
#if DEBUG_TEST
/**
 * @brief  Writes a single given character to the DEBUG_TERMINAL through I2C.
 *
 * @param  out: The character to write
 * @retval None
 */
HAL_StatusTypeDef printDebugChar(uint8_t out) {
	HAL_I2C_Master_Transmit(&hi2c1, DEBUG_TERMINAL, &out, 1, HAL_MAX_DELAY);
}

/**
 * @brief  Writes a given character array of given size to the DEBUG_TERMINAL through I2C.
 *
 * @param  out: The character array to write
 * @param  size: The size of the character array
 * @retval None
 */
HAL_StatusTypeDef printDebug(uint8_t* out, int size) {
	HAL_I2C_Master_Transmit(&hi2c1, DEBUG_TERMINAL, out, size, HAL_MAX_DELAY);
}
#else

/**
 * @brief  Placeholder in case debug mode is disabled
 *
 * @param  out: The character to write. Ignored
 * @retval HAL_OK
 */
HAL_StatusTypeDef printDebugChar(uint8_t out) {
	return HAL_OK;
}

/**
 * @brief  Placeholder in case debug mode is disabled
 *
 * @param  out: The character to write. Ignored
 * @retval HAL_OK
 */
HAL_StatusTypeDef printDebug(uint8_t* out, int size) {
	return HAL_OK;
}
#endif

/**
 * @brief  Write a given amount of 0's to the NFC tag, starting from address 0.
 *
 * @param  size: Amount of 0's to write
 * @retval None
 */
void wipeMemory(int size) {
	for (uint16_t addr = 0; addr < size; addr++) {
		  HAL_I2C_Mem_Write(&hi2c1, NFC_ADDR, (uint16_t) addr, 2, &zero, 1, 1000);
	  	  HAL_Delay(10);
	  }
}

/**
 * @brief  Write a given array of bytes to the NFC tag, starting at a given memory address.
 *         Ensures that the NFC tag is done writing before returning.
 *
 * @param  data: Pointer to the byte array to be written
 * @param  size: The amount bytes to write
 * @param  memAddr: The memory-address of the first byte
 * @retval HAL_StatusTypeDef
 */
HAL_StatusTypeDef writeMemory(uint8_t* data, int size, uint16_t memAddr) {
	HAL_StatusTypeDef status = HAL_I2C_Mem_Write(&hi2c1, NFC_ADDR, memAddr, I2C_MEMADD_SIZE_16BIT, data, size, HAL_MAX_DELAY);
	HAL_Delay(2);

	uint8_t count = 0;
	while(HAL_I2C_IsDeviceReady(&hi2c1, NFC_ADDR, 1, 5) != HAL_OK && count < 50) {
		HAL_Delay(5);
		count++;
	}

	return status;
}

/**
 * @brief  Write a given array of bytes to the data section of the NFC tag.
 *         Automatically selects the end of the data section increments the memory pointer (locally, not on the NFC tag).
 *
 * @param  data: Pointer to the byte array to be written
 * @param  size: The amount of bytes to write
 * @retval HAL_StatusTypeDef
 */
HAL_StatusTypeDef writeDataMemory(uint8_t* data, int size) {
	if (memPointer + size >= MEMORY_SIZE || memPointer < 9) {
		return 1;
	}

	HAL_StatusTypeDef status = writeMemory(data, size, memPointer);
	memPointer += size;

	return status;
}

/**
 * @brief  Saves the local memory pointer to the NFC tag.
 *
 * @retval HAL_StatusTypeDef
 */
HAL_StatusTypeDef saveMemPointer() {
	if (memPointer >= 9 && memPointer <= MEMORY_SIZE) {
		uint8_t buff[2] = {memPointer, (memPointer >> 8)};
		return writeMemory(buff, 2, MEM_POINTER_REG);
	}

	return HAL_ERROR;
}

/**
 * @brief  Scans the I2C bus for devices. Writes all addresses that respond to the NFC tag.
 *
 * @retval 0
 */
int I2CDeviceScan() {
	uint8_t final_addr = 0;

	/* ASSIGNMENT CODE BEGIN */
	/*
	__attribute__((unused)) HAL_StatusTypeDef resNfc = HAL_I2C_IsDeviceReady(&hi2c1, NFC_ADDR, 3, 5);
	__attribute__((unused)) HAL_StatusTypeDef recRtc = HAL_I2C_IsDeviceReady(&hi2c1, AM1805_ADDR, 3, 5);
	__attribute__((unused)) HAL_StatusTypeDef resAccel = HAL_I2C_IsDeviceReady(&hi2c1, ACCEL_ADDR, 3, 5);

	// I don't think this is needed as the loop below spans the whole address space, just like the three calls above
	// I actually used the unshifted ADDR as a macro but this should be fine as the driver hides the ADDR anyway
	__attribute__((unused)) HAL_StatusTypeDef resNewTemp = HAL_I2C_IsDeviceReady(&hi2c1, TMP117_ADDR << 1, 3, 5);
	*/
	/* ASSIGNMENT CODE END */

	// is this scanning the whole address space?
	for (uint8_t addr = 0; addr < 128; addr++) {
		  HAL_StatusTypeDef res = HAL_I2C_IsDeviceReady(&hi2c1, (uint16_t)(addr<<1), 3, 5);
		  if (res == HAL_OK) {
			  final_addr = (addr<<1);
			  HAL_I2C_Mem_Write(&hi2c1, NFC_ADDR, memPointer, 2, &final_addr, 1, 1000);
			  memPointer += 1;
		  }

		  HAL_Delay(10);
	  }

	  HAL_I2C_Mem_Write(&hi2c1, NFC_ADDR, memPointer, 2, &zero, 1, 1000);
	  memPointer += 1;

	  return 0;
}

/**
 * @brief  Enables all sensors that should be enabled
 *
 * @retval None
 */
void enableSensors() {
	if (accelEnable || tempEnable) {
		uint8_t enableAccel = 0b00010000; //low power mode, lowest frequency, 12 bit
		enableAccel = 0x3B;
		HAL_I2C_Mem_Write(&hi2c1, ACCEL_ADDR, ACCEL_CONTROL1, I2C_MEMADD_SIZE_8BIT, &enableAccel, 1, HAL_MAX_DELAY);
		enableAccel = 0x03;
		HAL_I2C_Mem_Write(&hi2c1, ACCEL_ADDR, 0x22, I2C_MEMADD_SIZE_8BIT, &enableAccel, 1, HAL_MAX_DELAY);
	} else {
		HAL_I2C_Mem_Write(&hi2c1, ACCEL_ADDR, ACCEL_CONTROL1, I2C_MEMADD_SIZE_8BIT, &zero, 1, HAL_MAX_DELAY);
	}

	/* ASSIGNMENT CODE BEGIN */
	if (newTempEnable) {
		// set the sensor to shutdown mode, 1 measurement only
		tmp117WriteReg(&hi2c1, TMP117_CONFIG_REG, TMP117_DEFAULT_CONFIG);
	}
	/* ASSIGNMENT CODE END */

	if (pdEnable) {
		HAL_ADCEx_Calibration_Start(&hadc, ADC_SINGLE_ENDED);
	}

}
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
